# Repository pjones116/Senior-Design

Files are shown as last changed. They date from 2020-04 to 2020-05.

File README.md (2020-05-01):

# User Manual
## __Back End and Physical Setup__:
#### Image the Raspberry Pi:
•	The official guide for this process can be found here: https://www.raspberrypi.org/documentation/installation/installing-images/

•	For the purposes of this generation of the product, our team used Raspbian GNU / Linux 9, also known as Stretch, but the OS version for the system should have little influence on proper operation

#### Connect the Pi to basic peripherals and boot:
•	Connect mouse and keyboard via USB

•	Connect HDMI cable to external monitor

•	Connect Ethernet cable for wired network connection (optional, only needed for setup)

•	Connect the Pi to wall power adapter

•	Boot into Raspbian or preferred OS

#### Enable system interfaces:
•	Once booted in, click on the Raspberry Pi symbol to open the system menu

•	Navigate down to “Preferences” and open the “Raspberry Pi Configuration” tab

•	Navigate to the “Interfaces” tab and ensure that Camera, SSH, VNC, and I2C are enabled

#### Setup remote monitoring webserver on the Pi:
•	Pagekite is used to assign hostnames to outward facing VNC addresses to make remote monitoring possible from anywhere

•	Sign up for Pagekite here: https://pagekite.net/signup/

•	Follow the guide at the following page: https://pagekite.net/support/quickstart/

•	Once initial setup is completed, two kites should be added by executing the following from command line:

  -	“python2 pagekite.py --add 80 <site_name>.pagekite.me”
  
  -	“python2 pagekite.py --add 5900 raw:vnc.<site_name>.pagekite.me:5900”

•	Both of these hostnames need to be up at all times and, after their creation, can be launched using the following from command line:

  -	“python2 pagekite.py 80 <site_name>.pagekite.me”

  -	“python2 pagekite.py port# raw:vnc.<site_name>.pagekite.me:5900”

•	This application’s website contains instructions on how to run this program from startup, if desired

#### Setup VNC monitoring on remote machine:
•	Download VNC Viewer by RealVNC on the machine the Pi will be monitored from

•	Navigate to preferences and locate the “Proxy” tab

•	Select the options to “Use these proxy settings”

•	Enter the following values:

  -	Server: vnc.<site_name>.pagekite.me:443

  -	Type: HTTP Connect

  -	User / Pass: pi / raspberry (initial image user / pass)

•	You can then connect via VNC to the Pi via the address vnc.<site_name>.pagekite.me:5900

#### Share SSH keys between the Pi and data server:
•	From the Raspberry Pi, generate an SSH key by executing the following on command line: 
  
  -	“ssh-keygen”

•	Then copy this key to the remote data server by executing the following: 

  -	“ssh-copy-id –i ~/.ssh/id_rsa.pub <X.X.X.X>”

•	This step is absolutely vital for this application’s performance and can be tested by attempting to SSH to the remote data server without password:

  -	“ssh <X.X.X.X>”

#### Setup Redis-Server on the Pi:
•	Redis-Server is used implement a job queuing process processing data from the application

•	The setup process can be found at the following: https://habilisbest.com/install-redis-on-your-raspberrypi

•	Once Redis is properly setup, this queue webserver should be run constantly when data is being processed by doing the following from command line:

  -	“redis-server”

#### Setup SQL Server on data server:
•	Both SQL Server and the SQL Command Line Tools should be installed on the data server

•	The following process should be followed:

  -	https://docs.microsoft.com/en-us/sql/linux/quickstart-install-connect-ubuntu?view=sql-server-ver15
  
  -	Please note, an Ubuntu based server is currently deployed for this group, but Microsoft provides installation guides for these tools for most common operating systems

•	Once SQL Server is properly setup, a table with the following columns and data types should be created (Please note: currently, all variables are VARCHAR type)

  -	Timestamp – VARCHAR
  
  -	pH – FLOAT
  
  -	Conductivity – FLOAT
  
  -	Temperature – FLOAT
  
  -	Humidity – FLOAT
  
  -	Image Name – VARCHAR

#### Setup ImageMagick on data server (optional):
•	ImageMagick can be used to view images via X server when a machine establishes an SSH connection with the data server

•	The following shows the setup process for a typical Ubuntu machine: https://linuxconfig.org/how-to-install-imagemagick-7-on-ubuntu-18-04-linux

•	In order to launch the X server on startup of the SSH session, simply type the following when first connecting:

  -	“ssh <user>@<X.X.X.X> -X”

•	Then, in order to display any image type the following on command line, once inside the image’s directory:

  -	“display <filename>.<extension>”

•	If continual issues occur with displaying images, make sure the $DISPLAY environment variable is set correctly on your data server by executing the following:

  -	“export DISPLAY=localhost:0.0”

#### Setup full peripherals:
•	Connect the PiCamera via GPIO ribbon the Pi’s camera port

•	Connect the Atlas T3 Tentacle hat to the Pi’s GPIO header and attach the appropriate Atlas sensors to their respective serial cable header

•	Attach the GPIO ribbon cable to the T3’s GPIO header extension, then connect a breadboard on the ribbon cable

•	Connect all additional sensors to their respective GPIO ports on the ribbon cable’s breadboard connector

•	Attach battery powering system, lower device into enclosure and properly attach sensors and camera to arms

#### Download application package from Github:
•	Download full application (3 scripts) from Github and create an appropriate environment for them (i.e. create and name a folder solely for holding the scripts)

•	Establish a folder called “capstone” on the Pi’s desktop, which will be used for storing the processed data and images

#### Download Python packages for scripts:
•	Execute the following from the command line to install a Python package:

  -	“pip install <pkg_name>”

•	The following is a list and description of all Python packages needed to run this application:

  -	time – Used to implement wait periods, timings
  
  -	sys – Used to force clean exit from script on error outs
  
  -	OS – Used to execute CMD commands from inside script
  
  -	subprocess – Used to call CMD subprocesses from inside script (i.e. rsync calls)
  
  -	picamera – Used to operate and manipulate Pi camera
  
  -	datetime – Used to establish time stamped naming conventions
  
  -	RPi.GPIO – Used to operate Pi GPIO ports
  
  -	Adafruit_DHT – Used to gather temperature and humidity data from Adafruit DHT11 or DHT22 sensor
  
  -	IO – Used to create and implement filestreams
  
  -	fcntl – Used to interact with I2C parameters for Atlas sensors
  
  -	string – Used to interact with and manipulate strings
  
  -	copy – Used to move I2C parameters between addresses by copying values under certain specified conditions
  
  -	RQ – Used to simply implement a Redis job queue (note: this is unofficial)
  
  -	Redis – Used to connect to Redis queue from inside script (note: this is official)
  
  -	Pyodc – Used to setup script connection to SQL Server 

#### Edit variable information in scripts:
• atlas.py – queue name for Redis queue, username and IP for data server, rsync folder name on data server

•	atlas_upload.py – queue name for Redis queue, connection details for SQL Server on data server, schema and table names for SQL Server table

#### Script details:
•	atlas.py:

  -	Takes sensor readings and images, submits data to Redis queue and uploads CSV and images to directory on data server
  
  -	Run at user’s discretion (i.e. run when user wants to run an experiment)
  
  -	Execute with the following: “python atlas.py”

•	atlas_worker.py:

  -	Acts as middleman and takes enqueued data to be submitted to queue and pushed to the correct script
  
  -	This script can be left running at all times due to low CPU and memory impact, as it will process results any time they are submitted
  
  -	Execute with the following: “python atlas_worker.py <queue_name>”

•	atlas_upload.py:

  -	Uploads the queued data to the remote data server’s SQL Server table
  
  -	NEVER interacted with by the user, this script is only used when called from the main atlas.py

## __System Operational Notes__:
•	Python version to be used – 2.7.13

  -	Though Python 2.7 is going to be considered fully deprecated soon, the only way that the current build works with Atlas’ provided I2C software is if it is used
  
  -	NOTE: ensure that the relevant version of Pip is deployed for installing packages for the correct version of Python

•	Constantly running scripts

  -	The easiest way to implement the technologies discussed in this guide without too much maintenance is to have several scripts     continually run (or to add them to your Bash configuration for launch on startup)
  
  -	It is recommended that both Pagekite addresses (main and VNC), atlas_upload, and redis-server stay continually running

•	This enables the application to run with end-to-end success by only executing the main atlas.py

## __Front End Setup__:
•	This project is uses a React front end app that is written in JavaScript.

•	Currently the code can be seen on a front-end GUI. However, due to some impediments related to the Coronavirus it is very basic and there is no user experience.

•	Information and documentation for React can be found here: https://reactjs.org/

•	The connection to the front-end is made in the Index.js file

•	To setup the environment for into the terminal and run the following:

  -	mkdir “folder name”
  
  -	touch package.json
  
  -	npm init -y

• Insert the code into the index.js file

• Install the following packages:
  
  -	yarn add express 
  
  - yard add mysql 
  
  -	yarn add cors
  
  -	yarn add react

•	In order to run the front end code, run the following command: ‘nodemon Index.js’

• Ensure that you are in the correct folder when running the code

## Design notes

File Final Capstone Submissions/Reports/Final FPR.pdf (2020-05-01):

The George Washington University School of Engineering and Applied Science Department of Electrical and Computer Engineering

ECE 4920W - 30

Final Product Review
Low Cost, Remote Data Acquisition Platform for In Situ Biological and Fluidic Measurements

Rachel Zaltz, Computer Engineering Connor Kraft, Computer Engineering Phillip Jones, Electrical Engineering

Professor Aslani, Professor Bulusu April 22, 2020

Final Design Review

Abstract (R)

A low-cost data acquisition platform will be designed and assembled to increase the ease of dynamic in situ data collection from confined isolated environments such as incubators. The aim of this project is to record humidity, temperature, PH, turbidity, time-stamped imaging, and various other sensor data at user-specified intervals. The device will remain physically independent of the space outside the incubator by using a modular power supply and network connection. The device will run independently of a power supply for the duration of the experiment and wirelessly send the desired data to a remote user. The device will advance research in cellular and polymetric interactions with indirect measurement and imaging in incubators.

Table of Contents
Table of Contents | 3
1. | Introduction (R) | 6
2. | Impacts and Effects (P) | 6
2.1. | Public Health | 6
2.2. | Safety | 6
2.3. | Welfare | 6
2.4. | Global | 6
2.5. | Social | 7
2.6. | Cultural | 7
2.7. | Environmental | 7
2.8. | Economic | 7
3. | Overall System Requirements and Specifications (All) | 7
4. | Approach to Overall Design (C) | 8
4.1. | Current Design | 8
4.2. | Evolution of Current Design | 8
5. System and Subsystems (Modules) Functional Diagrams, Requirement and Specifications
| (All) | 9
5.1. | Raspberry Pi Subsystem Requirements and Specifications | 9
5.2. | Sensor Subsystem Requirements and Specifications | 9
5.2.1. Raspberry Pi GPIO Controller Description | 10
5.2.2. LED Lights Description | 10
5.2.3. Raspberry Pi Camera Description | 11
5.2.4. Pi Tentacle Hat Description | 11
5.2.5. Conductivity Sensor Description | 11
5.2.6. pH Sensor Description | 11
5.2.7. Temperature & Humidity Sensor Description | 11
5.3. | User Interface Subsystem Requirements and Specifications | 11
5.4. | Power Management Subsystem Requirements and Specifications | 12
5.4.1. Charge Protection Circuit Requirements and Specifications | 12
5.4.2. Battery Requirements and Specifications | 12
5.4.3. Voltage Converter Circuit Requirements and Specifications | 12
6. | Module Design (All) | 13
6.1. | Raspberry Pi Subsystem | 13
6.2. | Sensor Interface Subsystem | 13

6.3. | User Interface Subsystem | 13
6.4. | Power Management Subsystem | 14
7. | Design Changes Since FDRF | 14
8. | Module and System Tests | 14
8.1. | Raspberry Pi Subsystem Tests | 15
8.2. | Sensor Subsystem Tests | 15
8.3. | User Interface Subsystem Tests | 15
8.4. | Power Management Subsystem Tests | 16
9. | Applicable Standards (All) | 16
9.1. | Probes | 16
9.2. | Raspberry Pi | 17
9.3. | System | 17
9.4. | Hardware | 17
9.5. | Protocols | 17
10. | Summary and Conclusions (R) | 18
11. | References | 18
12. | Appendices | 18
12.1. Timeline Estimation and Milestones | 18
12.2. Economic Analysis | 20
12.3. Part List | 22
12.4. Qualifications of Key Personnel | 23
12.5. Intellectual Contributions | 24
12.6. Teaming Arrangements | 24
12.7. User Manual | 24
12.8. Mechanical Drawings | 28
12.9. GUI Screenshots | 31
12.10. Code | 31

Table of Figures:

1. Introduction (R)
The low-cost data-acquisition platform will be designed to increase dynamic in situ data collection in confined and isolated environments. Currently, when an experiment is performed within an incubator for a long period of time, lab technicians are unable to open the confined environment until the experiment has been completed in its entirety. This results in a loss of crucial data points as the experiment is progressing within the incubator. Currently, the data cannot be obtained during the duration of the experiment and this results in the loss of many crucial data points. A low-cost data acquisition platform would increase data collection in in situ environments.
Currently, there are only a few products that solve the issue at hand. Some of the best products are from Dickson Data, such as the DicksonOne. These products only allow for a small set of sensors and lack more advanced sensor technology and cameras. They are also very expensive, with the cheapest model being $350. Each individual sensor costs over 100 dollars and requires a paid subscription to use some of the more advanced features. Overall, a product does not exist that meets all of the design requirements for this task.
This project looks to implement a system which can gather data within a closed incubator and send that data to a user on any remote computer. The data is gathered from multiple sensors including temperature, humidity, pH, turbidity, and time stamped images. This data is gathered at a time interval which can be specified by the user to allow for greater flexibility of the system. When data is not being gathered, sensors are turned off in order to save power and conserve energy. This data is then sent to a computer using a Wifi connection so that it may be viewed by the user.
2. Impacts and Effects (P)
2.1. Public Health
Our product has no overall effects or impacts on public health in general. While research generated by the project or by employment of our device may positively impact public health, our system itself does not improve public health.
2.2. Safety
See reasoning for public health.
2.3. Welfare
Our project is also heavily focused on the promotion of ease of access of data acquisition. Having a fully wireless module that performs all functionality via remote GUI, with no impact on environment conditions inside the experiment, is an extremely productive option to the alternatives. This will increase the opportunities to have full experiment length data measurement, as well as make the data acquisition process smoother in general.
2.4. Global
As spoken about in the welfare section, this project will make overall data acquisition easier for the user. In addition, users will be able to run data acquisition experiments in areas without wired power; however, the data would have to be transferred locally at some point instead of being dumped wirelessly. This could have potential to drive this system as an alternative for taking large-scale equipment to remote research sites.

2.5. Social
This project will make taking data from environments like an incubator more convenient and hands free, increasing the social wellbeing of the communities it will be deployed in.
2.6. Cultural
Our project has little to no impact on the cultural standing of the community.
2.7. Environmental
Our project has little to no impact on the environment, as opposed to alternative options. As stated before, our project itself has no impact on this, but the research where it is employed could very well be beneficial.
2.8. Economic
Our project has an economic benefit, in that the cost effectiveness of the product is much more productive than its next best alternatives. Due to the low cost to employ this device, money will be able to be reallocated to other research needs.
3. Overall System Requirements and Specifications (All)
System Level Requirements | System Level Specifications
The device will operate with a lithium ion battery pack. | The device shall be able to run on a lithium ion battery pack.
The device will have a long battery life, so the device does not have to be removed from the incubator. | The device shall be able to last on the battery pack for the duration of the experiment (minimum 1 day - maximum 4 weeks).
The device will take pictures of the test environment. | A Pi camera must be used to take pictures of the test environment at user specified intervals.
The device will have a light source for the test environment. | The device must conserve battery by only using the lights when needed (e.g., taking a picture) or when the user specifies.
The device will conserve battery with 2 different modes: sleep and active. | The device shall be in sleep mode when measurements and images are not being taken.
The device will measure pH. | The device shall be able to measure the pH of the solution from 0 to 14 at +/-

| 0.001 increments using a pH probe, with an accuracy of +/- 0.002.
The device will measure humidity and temperature. | The device shall be able to measure humidity from 20 to 80% with an accuracy of +/- 5% and temperature from 0 to 50 degrees C with an accuracy of +/- 2 degrees C using Pi HAT sensors.
Th device will measure turbidity. | A turbidity probe shall be used to measure the amount of light scattered by the solids in the solution.
Th device will measure electrical conductivity. | A conductivity probe shall be used to measure the electrical conductivity of the solution from 5 to 200,000 micro-S/cm, with an accuracy of +/- 2%.
The device will be accessible to a remote user. | The device shall send data to a GUI that can be accessed remotely through a desktop and mobile application.
Communication will be enabled via Wifi on the device. | The device should be able to send data to a computer via the built in Wifi module on the Raspberry Pi 3+.
4. Approach to Overall Design (C & R)
4.1. Current Design
The goal of the project is to design a system which can gather data in a closed environment and send this data wirelessly to a remote user. The data gathered is specified by the sensors in section 6.2. The system can do this with only one input from the user, the data collection rate (every 30 seconds), and how long to gather data for (12 hours). These inputs and outputs are outlined in Figure 2 below. The flow of data from the user to system and system to user can be seen in Figure 1 below. Further, Figures 3-5 details the modules in more depth.
4.2. Evolution of Current Design
This design has shifted gears slightly amidst the current pandemic. Due to some constraints, not all testing was completed, and the user interface functions on a very minimal level. The overall goal of the project is maintained; however, we were not able to implement our design in a real testing space due to social distancing measures.

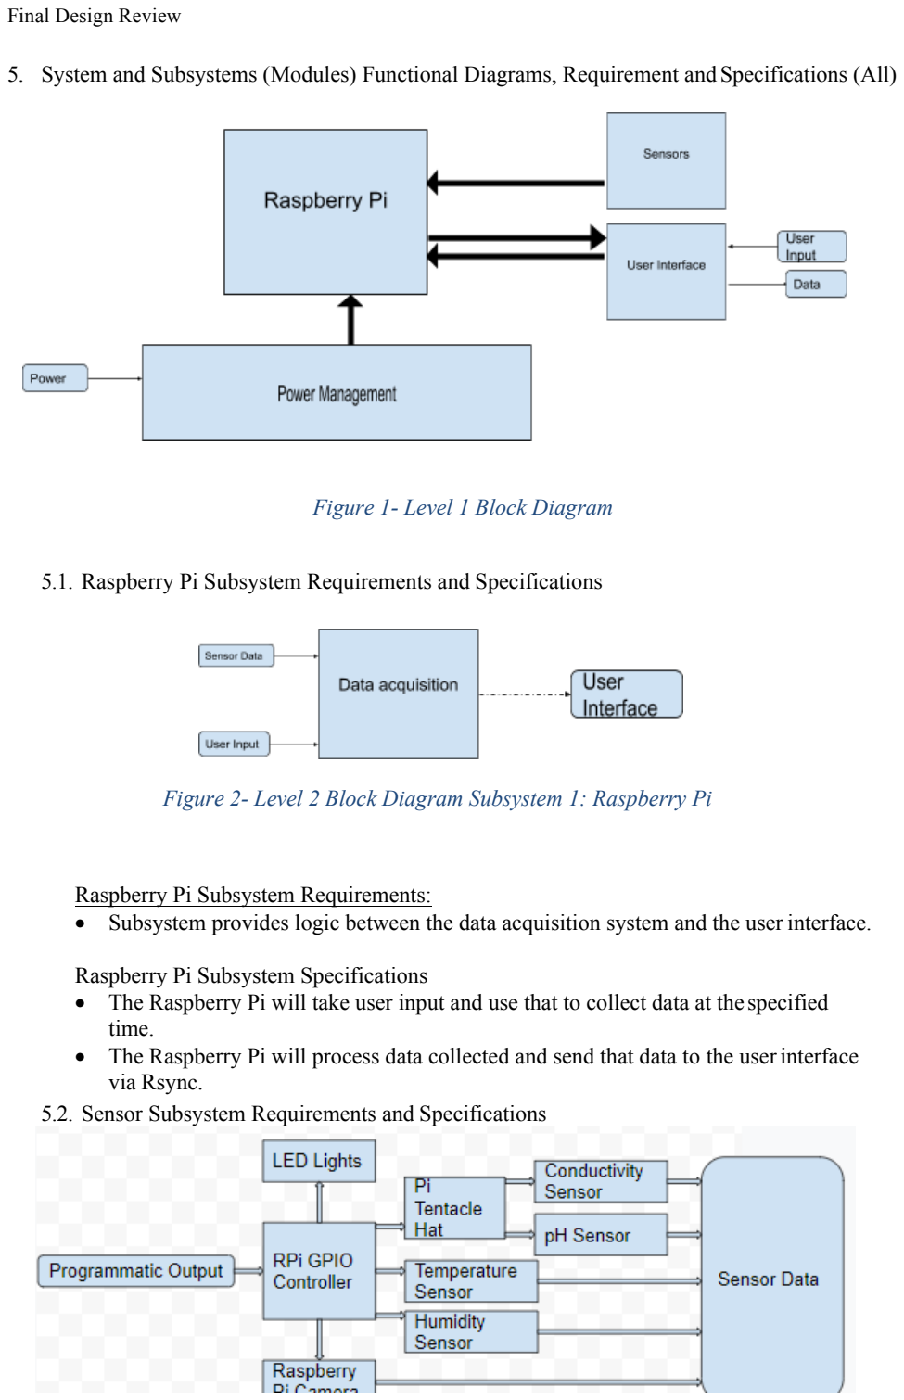
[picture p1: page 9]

5. System and Subsystems (Modules) Functional Diagrams, Requirement and Specifications (All)

Figure 1- Level 1 Block Diagram

5.1. Raspberry Pi Subsystem Requirements and Specifications

Figure 2- Level 2 Block Diagram Subsystem 1: Raspberry Pi

Raspberry Pi Subsystem Requirements:
- Subsystem provides logic between the data acquisition system and the user interface.

Raspberry Pi Subsystem Specifications
- The Raspberry Pi will take user input and use that to collect data at the specified time.
- The Raspberry Pi will process data collected and send that data to the userinterface via Rsync.
5.2. Sensor Subsystem Requirements and Specifications

Figure 3 - Level 2 Block Diagram Subsystem 2: Sensors

Sensor Subsystem Requirements:
- Subsystem provides data acquisition for system, using the inputs given via user program instructions.
- Subsystem sends user data back to program data stream.

Sensor Subsystem Specifications:
- The Raspberry Pi GPIO controller will translate the programmatic read instructionsto sensors readable inputs.
- The LED will inform each time the system is specified to take a reading.
- The Raspberry Pi camera will take a photo at each read interval.
- The Raspberry Pi Tentacle T3 hat will relay programmatic read instructions to the conductivity and pH sensors.
- The EZO conductivity and pH sensors will gather and relay sample conductivity and pH data at specified intervals.
- The temperature and humidity sensor will process and relay environmental condition data.
5.2.1. Raspberry Pi GPIO Controller Description
The Raspberry Pi GPIO controller provides the basis for sending and reading voltage levels to and from sensors. When provided with corresponding voltage, sensors will return their read value to the header. This information is then reformatted for user or program access.
5.2.2. LED Lights Description
A red LED shall be used to provide a notification system for the user. The light will blink each time a read is made on the system’s sensor array.

5.2.3. Raspberry Pi Camera Description
The camera connects to the MIPI camera serial interface on the Raspberry Pi via a 15- pin ribbon cable. It can take 3280 × 2464-pixel images.
5.2.4. Pi Tentacle Hat Description
The hat connects to the GPIO of the Raspberry Pi and outputs 3 BNC connections. It includes chips to handle the configuration of each individual sensor. It passes through the GPIO pins to allow for stacking of hats or connection of other parts.
5.2.5. Conductivity Sensor Description
The Atlas Scientific Conductivity Probe measures system level of conductivity from 5 to 200,000 uS/cm, with an accuracy of +/- 2%. The sensor will relay the environmental or sample level of conductivity at the user specified interval.
5.2.6. pH Sensor Description
The Atlas Scientific pH probe measures system levels of pH from 0 to 14, with an accuracy of +/- 0.002. The sensor will relay the environmental or sample level of pH at the user specified interval.
5.2.7. Temperature & Humidity Sensor Description
The Adafruit DHT11 probe measures environmental temperature and humidity. The humidity sensor measures from 20 to 90 room humidity with an accuracy of +/- 5%. The temperature sensor measures from 0 to 50 degrees Celsius with an accuracy of +/- 2%. The sensor will relay the environmental temperature and humidity data at user specified intervals.
5.3. User Interface Subsystem Requirements and Specifications

Figure 4 - Level 2 Block Diagram Subsystem 3: User Interface

User Interface subsystem requirements
- The data must be easily accessible to a remote user.

User Interface subsystem specifications
- The user must be able to access all experiment data from the system.

5.4. Power Management Subsystem Requirements and Specifications

Figure 5 - Level 2 Block Diagram Subsystem 4: Power Management

Power management subsystem requirements
- System supplies voltage to Raspberry Pi.
- System charges the battery.

Power management subsystem specifications
- The Raspberry Pi takes 5 Volts.
- A wall outlet will charge the battery.
5.4.1. Charge Protection Circuit Requirements and Specifications Charge protection circuit requirements
- Circuit optimizes the safe charging of the battery.

Charge protection circuit specifications
- The charge protection circuit will stop charging the battery at 100% charge.
- The charge protection circuit will monitor the charge level in each cell and keep each cell at the same level of charge.
5.4.2. Battery Requirements and Specifications
Battery Requirements
- The battery will supply power to the Raspberry Pi.

Battery Specifications
- The battery will charge from the charge protection circuit.
- The battery will output 12 Volts, which it will supply to the voltage conversion circuit.
- The battery will hold at least 200ah of charge
5.4.3. Voltage Converter Circuit Requirements and Specifications
Voltage converter circuit Requirements
- Circuit converts battery output to a lower voltage to supply Raspberry Pi.

Voltage converter Specifications
- The voltage converter will take 7V from the output of the battery and output 5V to power the Raspberry Pi.
6. Module Design (All)
6.1. Raspberry Pi Subsystem
The Raspberry Pi is the central computation and storage module for the system. It receives power from the power management module and receives input from programmatic user instructions. It runs experimental scripts and gathers data via input from attached sensors. It stores and exports data via Rsync / GUI / local storage.
A Raspberry Pi was chosen for this subsystem over other alternatives such as Beagleboard and Arduino. The Raspberry Pi was chosen for its low cost and its ability to meet the other specifications required by the project.
6.2. Sensor Interface Subsystem
The sensor module works via the Raspberry Pi’s GPIO header outputting programmatic instructions. Temperature and humidity are measured via sensor straight from this header, while all Atlas sensor data is taken through conversion to I2C over BNC via the Tentacle T3 Hat. In addition, the Pi Camera is powered from another GPIO slot on board. All received data from the sensors and camera are then stored locally and manipulated by programmatic instruction.
6.2.1. Camera
The Raspberry Pi camera was chosen due to the ease of connecting it to the Raspberry Pi. Other cameras were investigated, such as ones connected by USB, but none met the project needs.
6.2.2. Tentacle Hat
This module was chosen based on the choice of sensors. This module exists because of the following two sensors, so no alternatives were considered.
6.2.3. Conductivity Sensor
This sensor was chosen in conjunction with the client. Alternatives were not considered.
6.2.4. pH Sensor
This sensor was chosen in conjunction with the client. Alternatives were not considered.
6.2.5. Temperature and Humidity Sensor
Initially, a simple thermistor and different off-the-shelf humidity sensors were investigated. We decided on the Adafruit DHT1 due to its ease of use combining both sensors into one and the ease of connecting it to the system.
6.3. User Interface Subsystem
Input for the UI system consists only of data and information about each experiment being related remotely from central Raspberry Pi. The UI receives this information and presents it to the user visually and enables the user to interact with and download that data.

The UI will receive this information in real time via webserver file transfer.

6.4. Power Management Subsystem
This module supplies power to the rest of the system. This module was designed with the need for the system to be able to operate in spaces with no wall power. The charge protection circuit receives power from the wall and distributes it evenly across all cells in the battery, stopping when the cells are full. The charge protection circuit regulates the output of the battery, preventing them from being fully discharged. The voltage converter changes the voltage outputted by the battery to the 5V required by the Raspberry Pi.
6.4.1. Charge Protection Circuit
No alternatives have been considered for this module. The system requires a battery to run and needs a way to safely charge.
6.4.2. Battery
No alternatives have been considered for this module. A battery is a requirement for our system to run. A power test was not conducted due to the restrictions of the pandemic.
6.4.3. Voltage Converter Circuit
No alternatives have been considered for this module. The Raspberry Pi requires 5V to run and a voltage converter is needed to regulate the voltage from the battery.
7. Design Changes Since FDRF
Since the completion of the FDR, design changes have primarily been related to the data pipeline structure for this project. These changes were born out of a necessity to facilitate user interaction with this system, as well as to provide redundant options for data transfer and storage. In order to complete both of these tasks, a Redis queue was added for chronning data transfer jobs and keeping them active in the event of some kind of failure, and a remote data server was added for storage and organization.

At the current time, gathered data is collected and stored in labeled local directories on the Raspberry Pi. All relevant timestamps, sensor data, and image names are then queued by Redis and transferred to a SQL Server database running on the server. For the sake of redundancy, all relevant Raspberry Pi local files are then synced to a directory on this server. Redis allows for consistency in transfer and maintains the operating status of said transfer jobs, and the remote data server allows for easy data presentation by the front end and acts as a secondary storage location.

It is important to note that other than these changes, the primary structure and design for this project has remained consistent. Though completion of work related to the front end and battery circuit was hindered extremely by the current state of the Coronavirus outbreak, these portions of the project are still integral to its functionality and purpose. In order to craft a successful end-to-end product, these sections need to be implemented.

8. Module and System Tests

Note: while the tests discussed below were supposed to be run, due to the current Coronavirus outbreak affecting certain aspects of this project’s completion, alternate testing strategies were devised. An overall system test was performed with varying parameters for overall time and sensor reading interval. Our team felt that this was a productive testing plan to complete what could be done with the current situation.

The three tests devised to test the overall system, sensor accuracy over time, data transfer behavior, and system behavior under load are as follows:

- 1 hour test – 360 sensor readings
- 2.5 hour test – 50 sensor readings
- 8 hour test – 97 sensor readings
8.1. Raspberry Pi Subsystem Tests
Tests:
- Pi Stress Test - Run a worst-case scenario experiment and check that the Raspberry Pi continuously sends the data to the user and storage solution.
- Pi / Remote Storage Stress Test - Run alternate test case scenario with large set of data; and ensure the Raspberry Pi is able to complete a run of transferring multiple megabyte files continuously.

Specifications:
- The Raspberry Pi will take user input and use that to collect data at the specified time.
- The Raspberry Pi will process the data collected and send that data to the user interface via rsync.
8.2. Sensor Subsystem Tests
Tests:
- Stress Test - Run a worst-case scenario experiment (4 weeks sampling every 2 seconds) and check that the sensors collect data over the whole time period.
- Use sensors to measure known variables (such as a known room temperature or standard pH solution) to check accuracy.

Specifications:
- The Raspberry Pi GPIO controller will translate the programmatic read instructionsto the sensors.
- The LED will inform the user of each time the system takes a reading.
- The Raspberry Pi camera will take a photo at each read interval.
- The Raspberry Pi Tentacle T3 hat will relay the programmatic instructions to the Atlas sensors.
- The sensors will relay environmental condition data at each specified time interval.
8.3. User Interface Subsystem Tests
Tests:
- Test functionality of visually interactive components by activating themand observing outputs.
- Verify the application’s responsiveness on screen sizes for tablets (width: 1024/768 pixels), monitors (width: infinite pixels), and mobile devices (width: 480/320 pixels).

Specifications:
- The user must be able to access and observe current system status.
- The user must be able to access and observe all sensor readings and pictures taken over the course of an entire experiment.

Note: Due to the Coronavirus outbreak not all the User Interface tests were completed. In an ideal world where there is more time these tests should still be done.

8.4. Power Management Subsystem Tests
Tests:
- Verify that the maximum output of the subsystem is 5 volts to the Raspberry Pi and any attached equipment.
- Run a worst-case scenario experiment (4 weeks sampling every 2 seconds) and check that power is applied at appropriate levels for the entirety of the experiment.
- Monitor the shape of the battery during charging and system operation and observe any alterations that occur.
Specifications:
- The system will supply 5 volts to the Raspberry Pi and any attached equipment.
- The battery must last for the maximum possible duration of an experiment; for this project, that length is anticipated to be a maximum of 4 weeks.
- The charge protection circuit will stop charging the battery when it has reached 100% charge.
9. Applicable Standards (All)
9.1. Probes
NSF/ANSI-51 Section 4.1
Pi / Remote Storage Stress Test - Run alternate test case scenario with large set of data; and ensure the Raspberry Pi can complete a run of transferring multiple megabyte files continuously.

NSF/ANSI-51 Section 7.6.1
Glass and glass-like materials. Such materials shall not be used for direct food contact that are also subject to impact by hard objects during use such as countertops, tabletops, cutting boards, cooking surfaces, and food preparation utensils. This standard has the same use case as the previous one.

73/23/EEC
The aim of this directive is to ensure that electrical equipment cannot be placed on the market if, when installed and maintained, it endangers the safety of persons, domestic animals or property. This standard is for the probes and it ensures that there is no danger due to being electrocuted.

ISO/IEC 17025
ISO/IEC 17025 enables laboratories to demonstrate that they operate competently and generate valid results, thereby promoting confidence in their work both nationally and around the world. It also helps facilitate cooperation between laboratories and other bodies by generating wider acceptance of results between countries. This standard is applicable to this project since our product will be used in labs to gather results.
9.2. Raspberry Pi
EC 60950-1:2005
Mains and battery-powered general low voltage electrical equipment must follow safety standards related to temperature exposure, dust and moisture exposure, etc. This standard applies to operation of RaspberryPi 3B+.

EN 55022 CISPR 22
There are radio disturbance characteristic limits and methods of measurement for electrical equipment. This establishes uniform requirements for radio disturbance, standard operating conditions, and standard interpretations of testing results. It applies to all standard and networked operations of RaspberryPi 3B+.

EN 55024 CISPR 24
Tests and places standardized limitations for device electrostatic discharge, surges, power frequency magnetic fields, power interruptions, and RF interference.

Covers standard and networked operations of RaspberryPi 3B+ and all attached electrical equipment.

EN 300 328 V2.1.1
Wideband transmission systems; data transmission equipment operating in the 2.4 GHz ISM band using wide band modulation techniques. Limitations on output RF power and behavioral maintenance of networked equipment. Applies to networked operation of RaspberryPi 3B+.
9.3. System
IEC 62311:2019
Covers appropriate maintenance of equipment-generated exposure to electric, magnetic, and electromagnetic for devices operating from 0 Hz to 300 GHz. Standard limitations are applied to equipment via localized standards, applicable to this standard. Applies to the operation of full system.

EN 55032 CISPR 32
Procedural standard for limiting levels of spurious signals generated by multimedia equipment for electromagnetic protection in industrial, commercial, and residential environments. Applies to the operation of full system.
9.4. Hardware
ISO 4032:2012
Hexagon regular nuts (style 1) — Product grades A and B. Used in sizing holes for nuts and bolts to assemble enclosure.
9.5. Protocols
UM10204
Philips Semiconductors (now NXP Semiconductors) developed a simple bidirectional 2-wire bus for efficient inter-IC control. This bus is called the Inter-IC or I2C-bus. This standard is used for communicating between the Raspberry Pi and the sensors.

RFC 4256
The Secure Shell Protocol (SSH) is a protocol for secure remote login and other secure network services over an insecure network. This document describes a general-purpose authentication method for the SSH protocol, suitable for interactive authentications where the authentication data should be entered via a keyboard. This standard is useful to our project since it is how we are going about sending data wirelessly using Rsync.
10. Summary and Conclusions (R)

This semester, all major tasks with the sensors were completed; sensors were integrated fully with the back-end code. In addition to this, a front-end GUI and enclosure modeling were drafted in preparation for full system operation. On the front-end the user can fully see all the data as opposed to having to look in the database now. Final drawings for the enclosure were done, however not everything was printed due to the current situation. The system is ready to be tested for an experiment if time would allow.

This semester, several improvements were made to the overall efficiency and functionality of the system’s data pipeline. A Redis queue was added to monitor and schedule the submission of data to the project’s newly added data server. This server was deployed into a redundant storage scheme where all information stored locally on the Raspberry Pi is then subsequently transferred to it via Rsync. In addition to this, a SQL Server was deployed on this remote storage space to be implemented by the graphical interface. This SQL database serves not only as an efficient way to serve the information to a user over the internet, but also as a quick lookup table to ensure that the system is functioning properly via system diagnostics read at every sensor interval. Overall, the last semester has yielded great productivity in the track to completion of this project. The data pipeline is fully prepared to be deployed both online and as a storage solution for a wider-spread audience.

11. References

Unlock the Power of Pay. (n.d.). Retrieved from https://www.salary.com/

12. Appendices
12.1. Timeline Estimation and Milestones

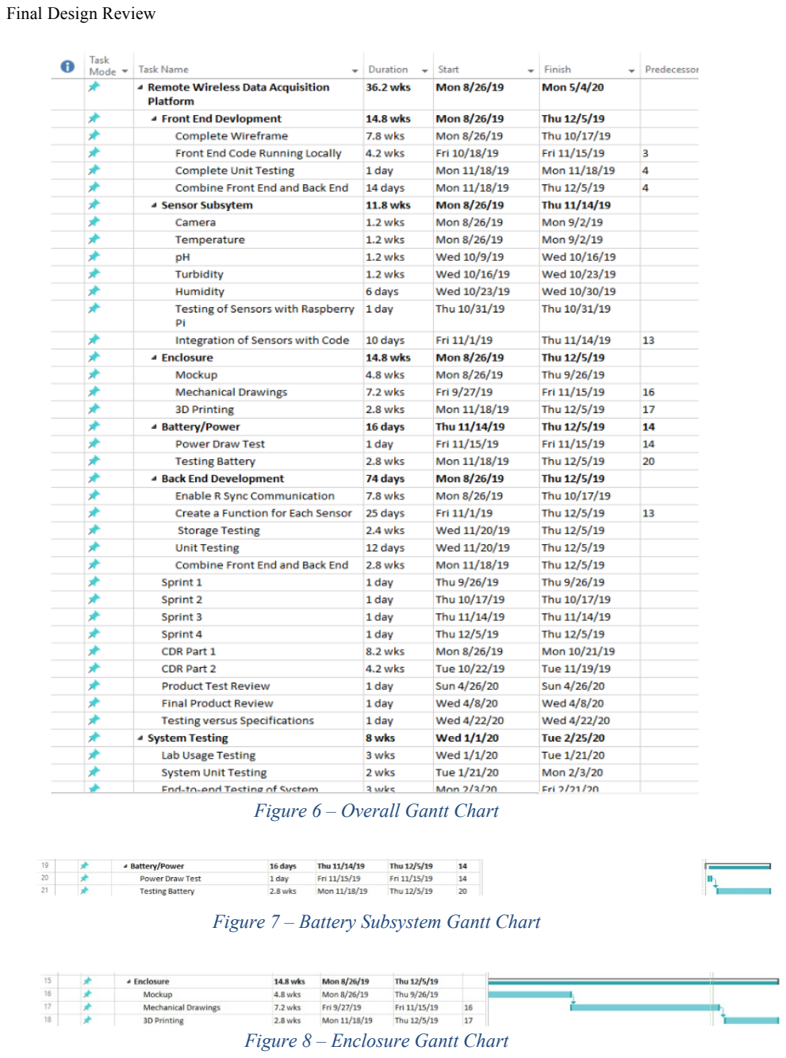
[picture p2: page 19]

Figure 6 – Overall Gantt Chart

Figure 7 – Battery Subsystem Gantt Chart

Figure 8 – Enclosure Gantt Chart

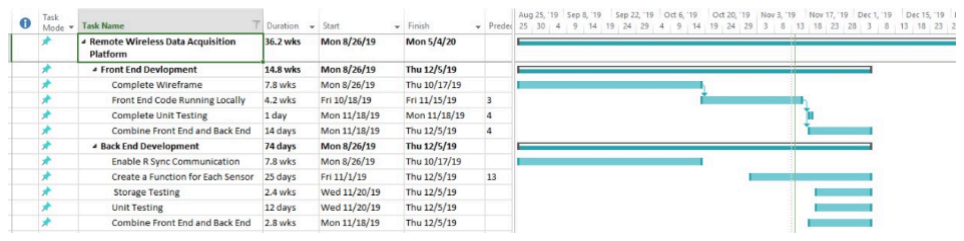
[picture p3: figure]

Figure 9 – Front/Back End Gantt Chart

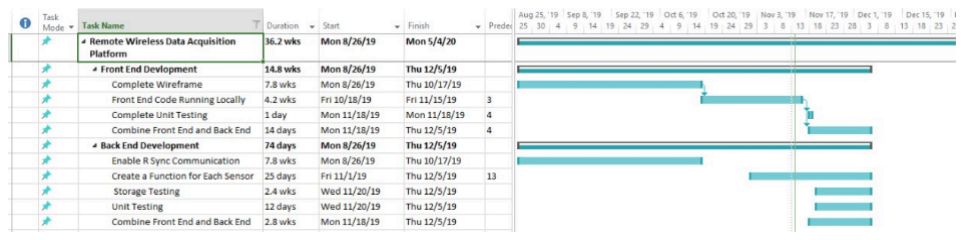
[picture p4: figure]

Figure 10 – Sensor Subsystem Gantt Chart

12.2. Economic Analysis

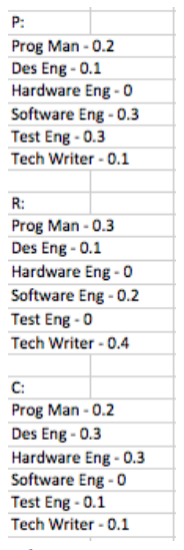
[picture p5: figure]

Figure 11 – Working Hours per Person

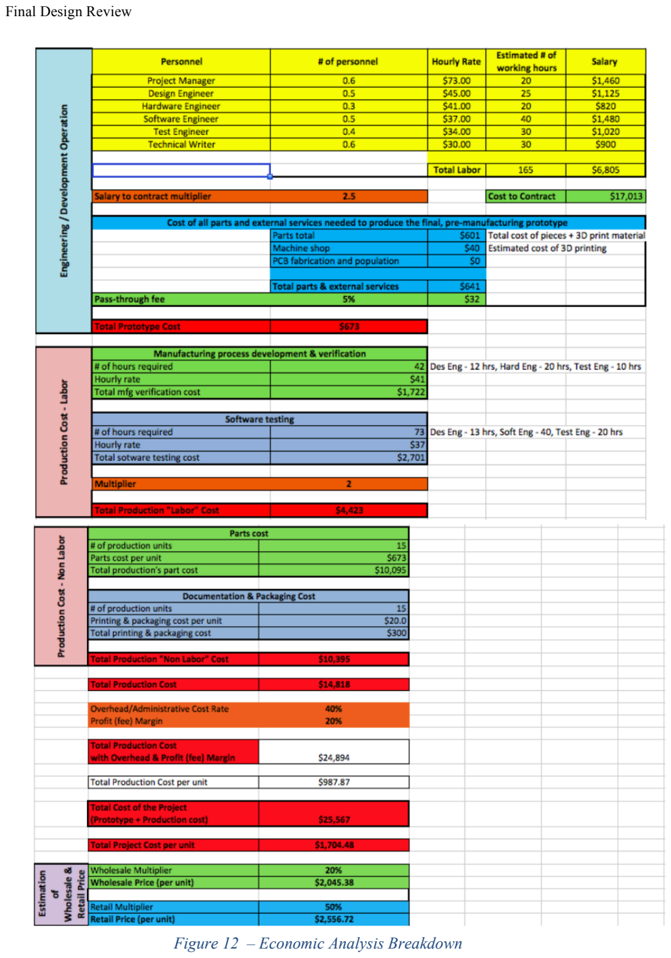
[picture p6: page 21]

Figure 12 – Economic Analysis Breakdown

This product would be offered as a good, with all the desired sensors and attachments wrapped in with the cost of the Raspberry Pi and the software application. The retail price of this product would be $2,556.72, as can be seen in the figure above. An additional option to use this software as a standalone option could also be released, where the user would provide their own Raspberry Pi and sensors, configuring the device on their own.

12.3. Part List
Part Name | Description | Manufacturer | Manufactur er’s Part # | Supplier | Cost ($) | Quantity
Single Board Computer | Raspberry Pi 3B + | Raspberry Pi | 3775 | Adafruit | 35.00 | 1
GPIO Extender | RPi GPIO Breakout Expansion Board & Ribbon | Arceli | ZB2L3 | Amazon | 7.99 | 1
Breadboard | Solderless Breadboard Kit | REXQualis | RQ-BK-002 | Amazon | 9.86 | 1
Resistor | 220 Ohm | E-Projects | 32121600 | Amazon | 6.00 | 1 (100 resistors)
Temperature-Humidity Sensor | DHT11 | Adafruit | 100502 | Amazon | 9.61 | 1
LED | Red Diffused LED | Jameco | 2152155 | Jameco | 0.59 | 5

Conductivity Sensor | Conductivity K 1.0 Kit | Atlas Scientific | EC-KIT-1.0 | Atlas Scientific | 215.00 | 1
pH Sensor | pH Kit | Atlas Scientific | KIT-101P | Atlas Scientific | 164.00 | 1
GPIO Hat | Tentacle T3 | Whitebox Labs for Atlas Scientific | TEN-T3 | Atlas Scientific | 105.00 | 1
Camera | RPi Camera Module V2-8 MP | Raspberry Pi | RPI-CAM-V2 | Amazon | 24.80 | 1
Ethernet Cable | CAT 6 Ethernet Cable | Mediabridge | 31-299-10B | Amazon | 5.84 | 1
12.4. Qualifications of Key Personnel
Rachel Zaltz’s qualifications make her a stellar candidate to work on this project. Her course work at the GWU includes Operating Systems, Microprocessors, Embedded Systems, Intro to C Programming will aid her in this project. [DZ2] Rachel’s wide knowledge of different programming languages allow her to adapt quickly. Her internship experience includes an extensive amount of front-end development, which will be useful towards the end of the project in building a user- friendly interface to view all the data.
Connor Kraft’s qualifications allow him to be a good team member. His work teaching children STEM classes over the summer, including teaching Python and Raspberry Pi courses, will aid in the overall design and troubleshooting of the project. Further, the teaching of 3D design and printing will be useful towards the end of the project when building an enclosure. His coursework at GWU includes Microprocessors, Embedded systems, and Circuit theory will all help in the hardware aspect of this project.
Phillip Jones has numerous experiences that are directly related to this project that will greatly facilitate with him making contributions. His coursework at GWU includes several Electronics Design classes, Microprocessor Systems, Introduction to C Programming, and Circuit Design. Phillip has worked for two semesters with SEAS computing as a Raspberry Pi student workshop director and has additional supplementary work experience with the same company. Lastly, he has extensive programming experience working on an automated data pipeline web application for Gamma Ray Burst behavioral analysis.

12.5. Intellectual Contributions
1. The group will purchase all sensors, power supply, and any other necessary fabrication materials.
a. The group will use these to fabricate all the above modules.
b. Sensors will be tested and calibrated for accuracy
2. We will design, implement, and test code to gather the sensor data.
3. We will implement Rsync to access the previously mentioned data wirelessly.
a. We will test this system with a wide variety of file sizes and file amounts
4. We will design, implement, and test a GUI that interacts with the previously mentioned code.
12.6. Teaming Arrangements
Throughout this project, all team members will work as a cohesive unit to ensure the product is designed properly. Each team member will lead one part of the project:
- Phillip will lead the group in implementing the physical code on the hardware.
- Connor will oversee testing the code and evaluating the results. He will also design an enclosure to house the final project.
- Rachel will build the GUI to display the data. She will also facilitate all documentation throughout the duration of the project.
12.7. User Manual

Setup Steps:
Image the Raspberry Pi:
- The official guide for this process can be found here: https://www.raspberrypi.org/documentation/installation/installing-images/
- For the purposes of this generation of the product, our team used Raspbian GNU / Linux 9, also known as Stretch, but the OS version for the system should have little influence on proper operation

Connect the Pi to basic peripherals and boot:
- Connect mouse and keyboard via USB
- Connect HDMI cable to external monitor
- Connect Ethernet cable for wired network connection (optional, only needed for setup)
- Connect the Pi to wall power adapter
- Boot into Raspbian or preferred OS

Enable system interfaces:
- Once booted in, click on the Raspberry Pi symbol to open the system menu
- Navigate down to “Preferences” and open the “Raspberry Pi Configuration” tab
- Navigate to the “Interfaces” tab and ensure that Camera, SSH, VNC, and I2C are enabled

Setup remote monitoring webserver on the Pi:
- Pagekite is used to assign hostnames to outward facing VNC addresses to make remote monitoring possible from anywhere
- Sign up for Pagekite here: https://pagekite.net/signup/
- Follow the guide at the following page: https://pagekite.net/support/quickstart/

- Once initial setup is completed, two kites should be added by executing the following from command line:
- “python2 pagekite.py --add 80 <site_name>.pagekite.me”
- “python2 pagekite.py --add 5900 raw:vnc.<site_name>.pagekite.me:5900”
- Both of these hostnames need to be up at all times and, after their creation, can be launched using the following from command line:
- “python2 pagekite.py 80 <site_name>.pagekite.me”
- “python2 pagekite.py port# raw:vnc.<site_name>.pagekite.me:5900”
- This application’s website contains instructions on how to run this program from startup, if desired

Setup VNC monitoring on remote machine:
- Download VNC Viewer by RealVNC on the machine the Pi will be monitored from
- Navigate to preferences and locate the “Proxy” tab
- Select the options to “Use these proxy settings”
- Enter the following values:
- Server: vnc.<site_name>.pagekite.me:443
- Type: HTTP Connect
- User / Pass: pi / raspberry (initial image user / pass)
- You can then connect via VNC to the Pi via the address vnc.<site_name>.pagekite.me:5900

Share SSH keys between the Pi and data server:
- From the Raspberry Pi, generate an SSH key by executing the following on command line:
- “ssh-keygen”
- Then copy this key to the remote data server by executing the following:
- “ssh-copy-id –i ~/.ssh/id_rsa.pub <X.X.X.X>”
- This step is absolutely vital for this application’s performance and can be tested by attempting to SSH to the remote data server without password:
- “ssh <X.X.X.X>”

Setup Redis-Server on the Pi:
- Redis-Server is used implement a job queuing process processing data from the application
- The setup process can be found at the following: https://habilisbest.com/install-redis-on-your-raspberrypi
- Once Redis is properly setup, this queue webserver should be run constantly when data is being processed by doing the following from command line:
- “redis-server”

Setup SQL Server on data server:
- Both SQL Server and the SQL Command Line Tools should be installed on the data server
- The following process should be followed:
- https://docs.microsoft.com/en-us/sql/linux/quickstart-install-connect-ubuntu?view=sql-server-ver15
- Please note, an Ubuntu based server is currently deployed for this group, but Microsoft provides installation guides for these tools for most common operating systems
- Once SQL Server is properly setup, a table with the following columns and data types should be created
- Timestamp – VARCHAR

- pH – FLOAT
- Conductivity – FLOAT
- Temperature – FLOAT
- Humidity – FLOAT
- Image Name – VARCHAR

Setup ImageMagick on data server (optional):
- ImageMagick can be used to view images via X server when a machine establishes an SSH connection with the data server
- The following shows the setup process for a typical Ubuntu machine: https://linuxconfig.org/how-to-install-imagemagick-7-on-ubuntu-18-04-linux
- In order to launch the X server on startup of the SSH session, simply type the following when first connecting:
- “ssh <user>@<X.X.X.X> -X”
- Then, in order to display any image type the following on command line, once inside the image’s directory:
- “display <filename>.<extension>”
- If continual issues occur with displaying images, make sure the $DISPLAY environment variable is set correctly on your data server by executing the following:
- “export DISPLAY=localhost:0.0”

Setup full peripherals:
- Connect the PiCamera via GPIO ribbon the Pi’s camera port
- Connect the Atlas T3 Tentacle hat to the Pi’s GPIO header and attach the appropriate Atlas sensors to their respective serial cable header
- Attach the GPIO ribbon cable to the T3’s GPIO header extension, then connect a breadboard on the ribbon cable
- Connect all additional sensors to their respective GPIO ports on the ribbon cable’s breadboard connector
- Attach battery powering system, lower device into enclosure and properly attach sensors and camera to arms

Download application package from Github:
- Download full application (3 scripts) from Github and create an appropriate environment for them (i.e. create and name a folder solely for holding the scripts)
- Establish a folder called “capstone” on the Pi’s desktop, which will be used for storing the processed data and images

Download Python packages for scripts:
- Execute the following from the command line to install a Python package:
- “pip install <pkg_name>”
- The following is a list and description of all Python packages needed to run this application:
- time – Used to implement wait periods, timings
- sys – Used to force clean exit from script on error outs
- OS – Used to execute CMD commands from inside script
- subprocess – Used to call CMD subprocesses from inside script (i.e. rsync calls)
- picamera – Used to operate and manipulate Pi camera
- datetime – Used to establish time stamped naming conventions
- RPi.GPIO – Used to operate Pi GPIO ports

- Adafruit_DHT – Used to gather temperature and humidity data from Adafruit DHT11 or DHT22 sensor
- IO – Used to create and implement filestreams
- fcntl – Used to interact with I2C parameters for Atlas sensors
- string – Used to interact with and manipulate strings
- copy – Used to move I2C parameters between addresses by copying values under certain specified conditions
- RQ – Used to simply implement a Redis job queue (note: this is unofficial)
- Redis – Used to connect to Redis queue from inside script (note: this is official)
- Pyodc – Used to setup script connection to SQL Server

Edit variable information in scripts:
- atlas.py – queue name for Redis queue, username and IP for data server, rsync folder name on data server
- atlas_upload.py – queue name for Redis queue, connection details for SQL Server on data server, schema and table names for SQL Server table

Script details:
- atlas.py:
- Takes sensor readings and images, submits data to Redis queue and uploads CSV and images to directory on data server
- Run at user’s discretion (i.e. run when user wants to run an experiment)
- Execute with the following: “python atlas.py”
- atlas_worker.py:
- Acts as middleman and takes enqueued data to be submitted to queue and pushed to the correct script
- This script can be left running at all times due to low CPU and memory impact, as it will process results any time they are submitted
- Execute with the following: “python atlas_worker.py <queue_name>”
- atlas_upload.py:
- Uploads the queued data to the remote data server’s SQL Server table
- NEVER interacted with by the user, this script is only used when called from the main atlas.py

System Operational Notes:
- Python version to be used – 2.7.13
- Though Python 2.7 is going to be considered fully deprecated soon, the only way that the current build works with Atlas’ provided I2C software is if it is used
- NOTE: ensure that the relevant version of Pip is deployed for installing packages for the correct version of Python
- Constantly running scripts
- The easiest way to implement the technologies discussed in this guide without too much maintenance is to have several scripts continually run (or to add them to your Bash configuration for launch on startup)
- It is recommended that both Pagekite addresses (main and VNC), atlas_upload, and redis-server stay continually running
! This enables the application to run with end-to-end success by only executing the main atlas.py

Front End Code Notes:
- This project is uses a React front end app that is written in JavaScript.
- Currently the code can be seen on a front-end GUI. However, due to some impediments related to the Coronavirus it is very basic and there is no user experience.
- Information and documentation for React can be found here: https://reactjs.org/
- The connection to the front-end is made in the Index.js file
- To setup the environment for into the terminal and run the following:
- mkdir “folder name”
- touch package.json
- npm init -y
- Insert the code into the index.js file
- Install the following packages:
! yarn add express
! yard add mysql
! yarn add cors
! yarn add react
- In order to run the front end code, run the following command: ‘nodemon Index.js’
- Ensure that you are in the correct folder when running the code.
12.8. Mechanical Drawings

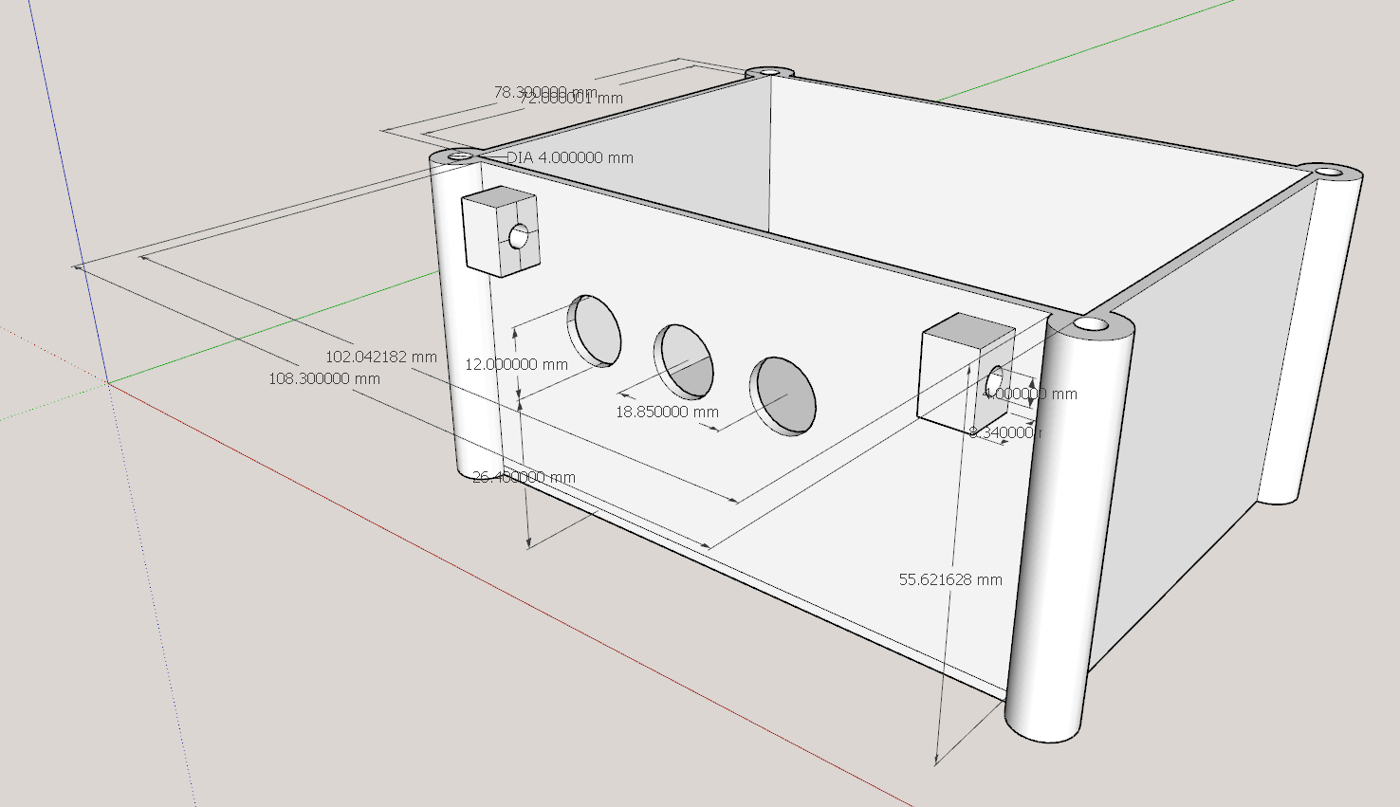
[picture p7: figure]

Figure 13 – Enclosure Bottom Piece

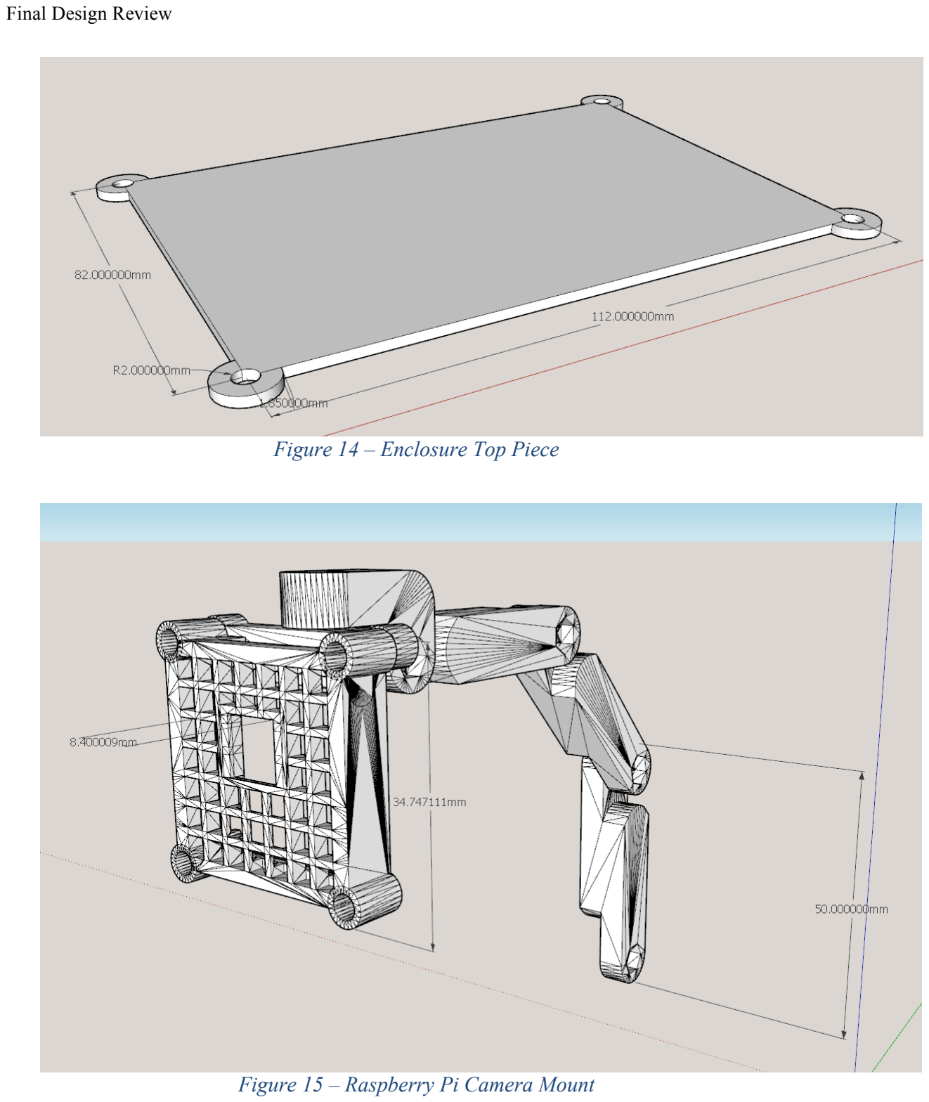
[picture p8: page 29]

Figure 14 – Enclosure Top Piece

Figure 15 – Raspberry Pi Camera Mount

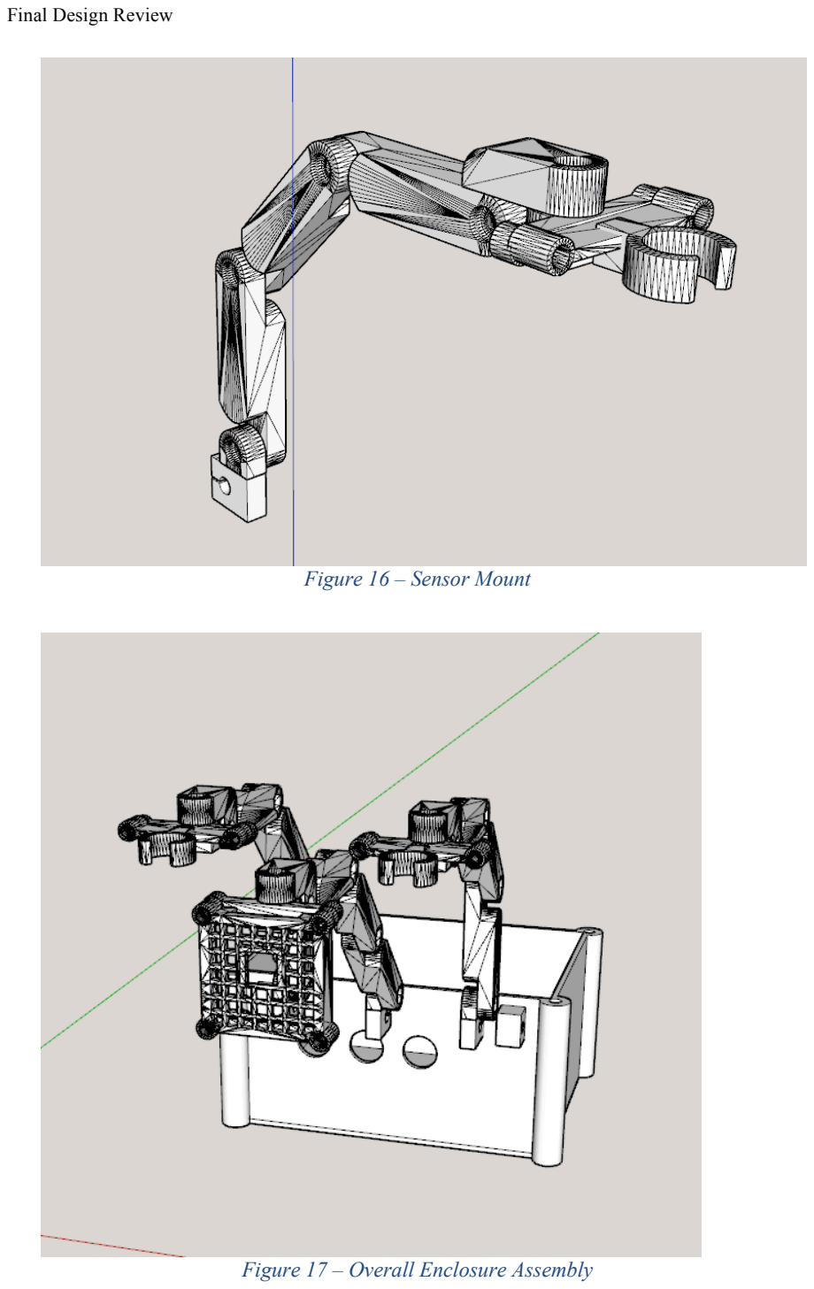
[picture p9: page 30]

Figure 16 – Sensor Mount

Figure 17 – Overall Enclosure Assembly

12.9. GUI Screenshots

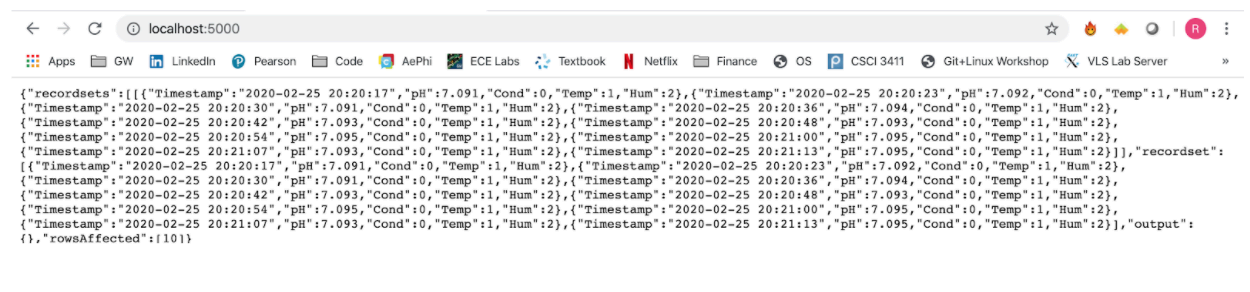
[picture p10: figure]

Figure 18 – Frontend Output

12.10. Code

// written by Rachel Zaltz
function ignoreFavicon(req, res, next) { if (req.originalUrl === '/favicon.ico') { res.status(204).json({nope: true});
} else {
next();
}
}
var express = require('express'); var cors = require('cors');
var app = express();
var React = require('react'); app.use(ignoreFavicon);
app.use(cors());
app.get('/', function (req, res) { var sql = require("mssql");

// config for your database var config = {
server:X.X.X.X',
user: 'XXXX',
port:XXXX,
password: 'XXXX',
database: 'XXXX'
};
// connect to your database sql.connect(config, function (err) {

if (err) console.log(err);
// create Request object
var request = new sql.Request();
// query to the database and get the records
request.query('select * from capstone.testing.example', function (err, recordset) { if (err) console.log(err)
// send records as a response
res.send(recordset);

});
});
});

// Listen on a specific host via the HOST environment variable var host = process.env.HOST || 'localhost';
// Listen on a specific port via the PORT environment variable var port = process.env.PORT || 5000;
var cors_proxy = require('cors-anywhere'); cors_proxy.createServer({
originWhitelist: [], // Allow all origins requireHeader: ['origin', 'x-requested-with'],
removeHeaders: ['cookie', 'cookie2']
}).listen(port, host, function() {
console.log('Running CORS Anywhere on ' + host + ':' + port); });
var server = app.listen(5000, function () {
console.log('Server is running..');
});
Connection from GUI to Back End Code

'''
ECE4925W - Final Capstone Submission, Spring 2020
Phillip Jones, Connor Kraft, Rachel Zaltz

final_atlas - takes data, organizes storage structure, submits queue request for transportation to storage server
final_atlas_worker - takes resulting data and actually submits to queue
final_atlas_upload - submits data to sql database on storage server

For detailed questions on packages used / scripts, please see User Manual Appendix and the FPR, in general

'''

import pyodbc | # Use to make Python connection to SQL Server on storage server
from rq import Queue | # Use to implement Redis queue actions
from rq import get_current_job | # Use to get information on submitted jobs
from redis import Redis | # Use to make Python connection to Redis server on RPi
from time import sleep | # Use to make program stop for period

def upload_to_db(data):
redis_conn=Redis()
q=Queue('atlas',connection=redis_conn,default_timeout=300)
# The following information currently works with the provided server

# Contact Mark Aglipay if you arrive with issues on the server / with the SQL Server application conn = pyodbc.connect(driver='{FreeTDS}',

server=X.X.X.X',
port='XXXXX',
database='XXXX',
uid='XXXX',
pwd='XXXX')
cursor=conn.cursor()

# Following data is taken from the constructed dictionary in final_atlas.py

# Data is out of order, but submits to server in correct order, due to how the queueing orders the information

# Sleep is used to reduce load on server between sensor readings / data commits tval=str(data.values()[3])

phval=str(data.values()[4])
condval=str(data.values()[5])
tempval=str(data.values()[0]) humval=str(data.values()[2])
imgval=str(tval + '.png')
expname=str(data.values()[1])
cursor.execute('INSERT INTO XXXX.XXXX.XXXX (Timestamp,pH,Cond,Temp,Hum,img_name,exp_name) VALUES (?,?,?,?,?,?,?)', tval,phval,condval,tempval,humval,imgval,expname)
conn.commit()
sleep(5)
return

Final Atlas Upload Python Code

'''
ECE4925W - Final Capstone Submission, Spring 2020
Phillip Jones, Connor Kraft, Rachel Zaltz

final_atlas - takes data, organizes storage structure, submits queue request for transportation to storage server
final_atlas_worker - takes resulting data and actually submits to queue
final_atlas_upload - submits data to sql database on storage server

For detailed questions on packages used / scripts, please see User Manual Appendix and the FPR, in general

All information in Class AtlasI2C was taken from Atlas Scientific's sample program for I2C device communication
'''
from atlas_upload import upload_to_db | # Called script from our application package
import time | # Use for actual timing
from time import sleep | # Use to stop scripts for period of time
import sys | # Use to control system level exit of program
import os | # Enables user to act on files outside program
import subprocess | # Use to invoke call to cmd
import picamera | # Use to control RPi camera
import datetime | # Use to get current datetime info
import RPi.GPIO as GPIO | # Use to interact with RPi GPIO pins
import Adafruit_DHT | # Stock module for temp/humidity sensor
import io | # Use to create file streams
from io import open | # Use to open files in file streams
import fcntl | # Use to access I2C parameters
import string | # Use to parse strings

import copy | # Use to implement copy as function of Python
from rq import Queue | # Allows for Redis job queueing
from rq import get_current_job | # Use for getting information about current job
from redis import Redis | # Use to make connection to Redis server
import psutil | # Use to produce system level diagnostic info about RPi

# Open camera, set resolution

camera = picamera.PiCamera()
camera.resolution = '1080p'

# Open GPIO pin 21, set for output as "flash" for photo GPIO.setmode(GPIO.BCM)

GPIO.setwarnings(False)
GPIO.setup(21,GPIO.OUT)

# Initialize temp/hum sensor

sensor = Adafruit_DHT.DHT11
pin = 23

# Initialize queue, open connection to atlas queue

redis_conn = Redis()
q = Queue('atlas', connection=redis_conn, default_timeout=300)

'''
All information in AtlasI2C is taken from the provided configuration of Atlas' I2C devices

This information can be altered as desired, please tread lightly when doing this,
as this can result in significant differences in operation for these sensors

In addition, this version has been altered, as the provided build encountered problems with sensor configuration and operation
'''

class AtlasI2C:
long_timeout = 1.5 | # Timeout needed to query readings / calibrations
short_timeout = 0.3 | # Timeout for regular commands
default_bus = 1 | # Default RPi I2C bus
default_address = 98 | # Default sensor address
LONG_TIMEOUT_COMMANDS = ("R", "CAL") # Wait for long period while reading SLEEP_COMMANDS = ("SLEEP", ) # Assign sleep commands

def __init__(self, address = default_address, bus = default_bus):
# Init 2 file streams, for reading and writing

self._address = address or self.default_address
self.bus = bus or self.default_bus
self._long_timeout = self.long_timeout
self._short_timeout = self.short_timeout
self.file_read = io.open(file="/dev/i2c-{}".format(self.bus), mode="rb", buffering=0) self.file_write = io.open(file="/dev/i2c-{}".format(self.bus), mode="wb", buffering=0) self.name = ""

def set_i2c_address(self, addr):
# Set I2C communications to slave address I2C_SLAVE = 0x703

fcntl.ioctl(self.file_read, I2C_SLAVE, addr) fcntl.ioctl(self.file_write, I2C_SLAVE, addr) self.address = addr

def write(self, cmd):
# Appends null character and send string over I2C cmd += "\00"

self.file_write.write(cmd.encode('latin-1'))

def handle_raspi_glitch(self, response):
if self.app_using_python_two():
return list(map(lambda x: chr(ord(x) & ~0x80), list(response))) else:
return list(map(lambda x: chr(x & ~0x80), list(response[1:])))

def app_using_python_two(self):
return sys.version_info[0] < 3

def get_response(self, raw_data):
if self.app_using_python_two():
response = [i for i in raw_data if i != '\x00' ] else:
response = raw_data

return response

def response_valid(self, response): valid = True
error_code = None
if(len(response)>0):
if self.app_using_python_two(): error_code = str(ord(response[0])) else:
error_code = str(response[0])

if error_code != '1':
valid = False

return valid, error_code

def get_device_info(self): if(self.name == ""):
return str(self.address)
else:
return str(self.address) + " " + self.name

def read(self, num_of_bytes=31):
raw_data = self.file_read.read(num_of_bytes)

response = self.get_response(raw_data=raw_data)
is_valid, error_code = self.response_valid(response=response)

if is_valid:
char_list = self.handle_raspi_glitch(response[1:])
result = "Success " + self.get_device_info() + ": " + str(''.join(char_list)) else:
result = "Error " + self.get_device_info() + ": " + error_code

return result

def get_command_timeout(self, command):
timeout = None
if command.upper().startswith(self.LONG_TIMEOUT_COMMANDS): timeout = self._long_timeout
elif not command.upper().startswith(self.SLEEP_COMMANDS): timeout = self.short_timeout

return timeout

def query(self, command):
self.write(command)
current_timeout = self.get_command_timeout(command=command) if not current_timeout:
return "sleep mode"
else:
time.sleep(current_timeout) return self.read()

def close(self):
self.file_read.close()
self.file_write.close()

def list_i2c_devices(self):
prev_addr = copy.deepcopy(self._address) i2c_devices = []
for i in range(0,128):
try:
self.set_i2c_address(i)
self.read(i)
i2c_devices.append(i)
except IOError:
pass
self.set_i2c_address(prev_addr)

return i2c_devices

def main():
# Allow for user input of experiment name

# MUST BE IN QUOTES, NO SPACES experiment_name = input("Input the name of the experiment: ")

# Timestamp name of data log file and enable write

d2 = datetime.datetime.now()
# Create local data dump folder

os.system('mkdir /home/pi/Desktop/capstone/' + experiment_name + '.' + d2.strftime('%Y.%m.%d-%H.%M.%S'))
# Create local data dump csv

csv = open('/home/pi/Desktop/capstone/'+ experiment_name + '.'+ d2.strftime('%Y.%m.%d-%H.%M.%S') + '/' + d2.strftime('%Y.%m.%d-%H.%M.%S') +'.csv', 'a')
# Create I2C port object

device = AtlasI2C()
try:
# FOR LOOP HARD CODED, CHANGE IN FUTURE (NUMBER OF READS)

# This loop turns on/off flash, takes photo in between, reads from each sensor

# Sensor info and system diagnostics are then organized and submitted to the Redis queue for storage server

# All info is then also saved to a local CSV, to be also transferred to storage server via rsync for i in range(0,5):

d = datetime.datetime.now()
print('\n')
print(d)
pict = d.strftime('%Y.%m.%d-%H.%M.%S')
picn = ('/home/pi/Desktop/capstone/' + experiment_name + '.'+ d2.strftime('%Y.%m.%d-%H.%M.%S') + '/' + pict + '.png')
print('Light on\t')
GPIO.output(21,GPIO.HIGH)
sleep(0.5)
print('Taking picture\t')
camera.capture(picn)
print('Light off, taking sensor data')
GPIO.output(21,GPIO.LOW)
#humidity, temperature = Adafruit_DHT.read_retry(sensor,pin)

# CHANGE THESE TEMP/HUM HARD CODED VALUES IN FUTURE temperature = 1.00

humidity = 2.00
device.set_i2c_address(99)
phstring = device.query('R')[11:] phstring = str(phstring)
device.set_i2c_address(100) condstring = device.query('R')[12:]
condstring = str(condstring)

data = {
'time' : d.strftime('%Y-%m-%d %H:%M:%S'), 'pH': phstring,
'conductivity': condstring,
'temperature': temperature,
'humidity': humidity,
'exp_name': experiment_name
}
log_data = {
'CPU usage' : psutil.cpu_percent(),

'CPU temp' : subprocess.check_output(['vcgencmd', 'measure_temp'], stderr=subprocess.STDOUT),
'RAM usage' : psutil.virtual_memory()[2]
}
job = q.enqueue(upload_to_db, data, result_ttl=86400) print('Current job on queue: %s\n' % (job.id,))
# Parsing and handling this information is both annoying and difficult,

# I reccomend leaving this scheme for the entirety of the project

# i.e. I reccomend not moving away from CSV as a secondary storage method csv.write(unicode('experiment: ' + str(data['exp_name']) + ',')) csv.write(unicode('time: ' + str(data['time']) + ','))

csv.write(unicode('pH: ' + str(data['pH']) + ',')) csv.write(unicode('conductivity: ' + str(data['conductivity']) + ',')) csv.write(unicode('temperaure: ' + str(data['temperature']) + ',')) csv.write(unicode('humidity: ' + str(data['humidity']) + ',\n')) csv.write(unicode('CPU usage: ' + str(log_data['CPU usage']) + ',')) csv.write(unicode('CPU ' + str(log_data['CPU temp'])[:-1] + ',')) csv.write(unicode('RAM usage: ' + str(log_data['RAM usage']) + ',')) csv.write(unicode('\n\n'))
sleep(3)
continue

# Proper exit: close camera, file, and invoke cmd to employ SSH file sync # Then exit at a system level

camera.stop_preview()
csv.close()
subprocess.call(['rsync','-avrPzh','/home/pi/Desktop/capstone','-e','ssh -p 22','user@X.X.X.X:~/'])
sys.exit()

# Improper exit: close camera, file, and brute force exit system

except KeyboardInterrupt:
camera.stop_preview()
csv.close()
print('\nClosed by keyboard interrupt.') sys.exit()

if __name__ == '__main__':
main()

Final Atlas Python Code

'''
ECE4925W - Final Capstone Submission, Spring 2020
Phillip Jones, Connor Kraft, Rachel Zaltz

final_atlas - takes data, organizes storage structure, submits queue request for transportation to storage server
final_atlas_worker - takes resulting data and actually submits to queue
final_atlas_upload - submits data to sql database on storage server

For detailed questions on packages used / scripts, please see User Manual Appendix and the FPR, in general

This program was provided entirely via the RQ setup guide

Launch Redis server first, type the following on cmd: "redis-server"

Launch with the following on cmd: "python final_atlas_worker.py atlas"

This names the queue that jobs will be submitted to

This script acts as middleman transport, can be left running at all times (script works automatically) '''

import sys
from rq import Connection, Worker

with Connection():
qs = sys.argv[1:] or ['default']
w = Worker(qs)
w.work()

Final Atlas Worker Python Code

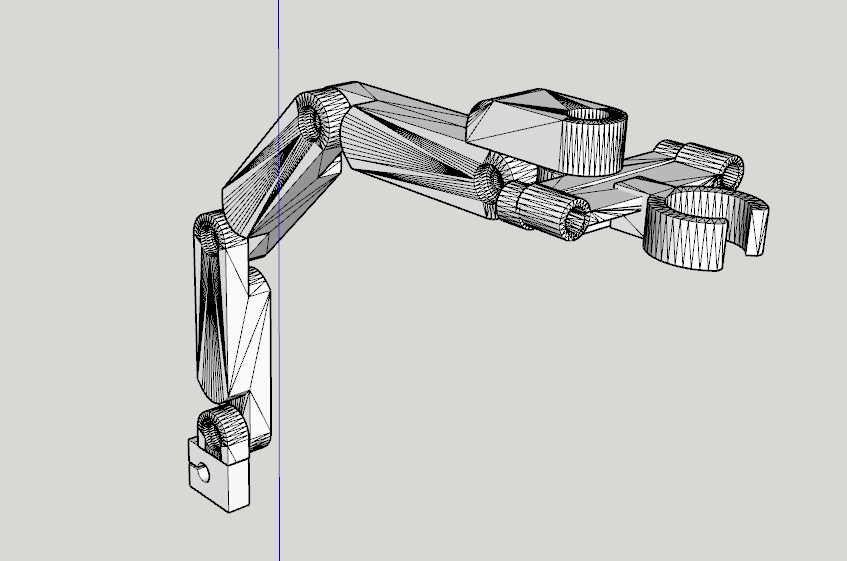
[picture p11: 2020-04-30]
Mechanical_Designs/Sensor_arm.PNG

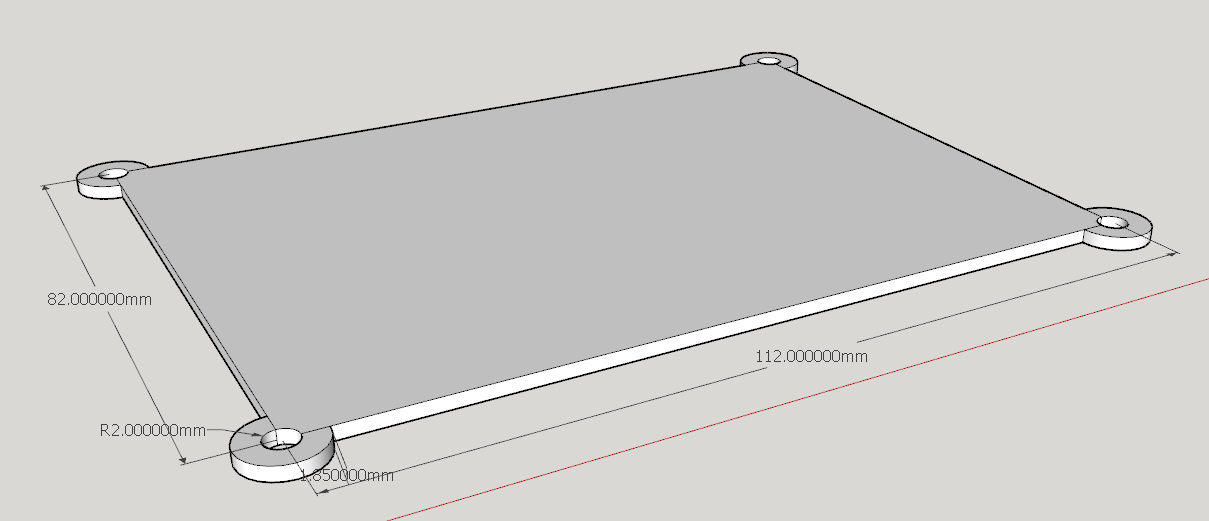
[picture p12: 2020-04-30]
Mechanical_Designs/case_top.PNG

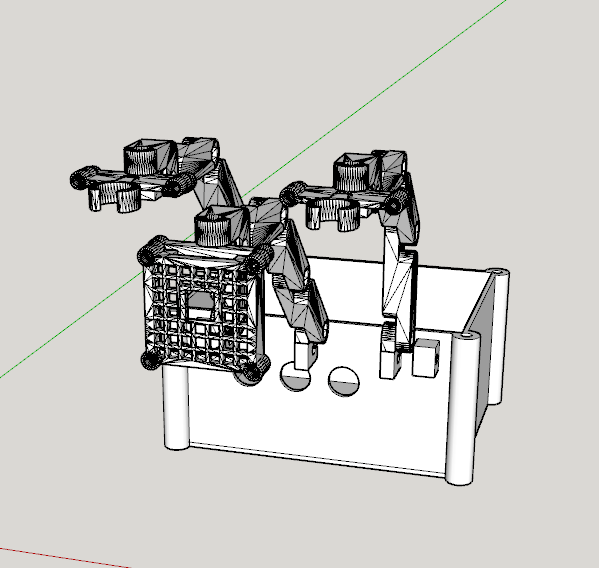
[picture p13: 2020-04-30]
Mechanical_Designs/All_together.PNG

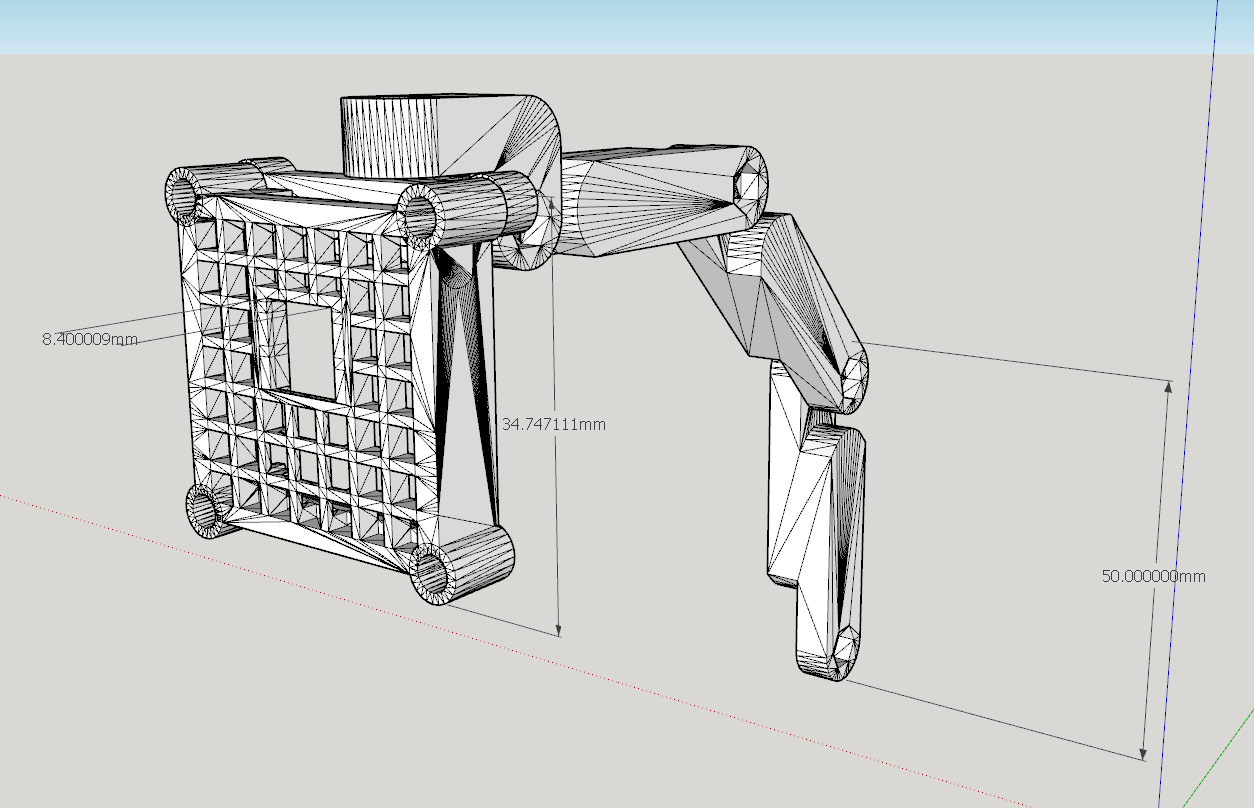
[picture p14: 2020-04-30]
Mechanical_Designs/Pi_camera_arm.png

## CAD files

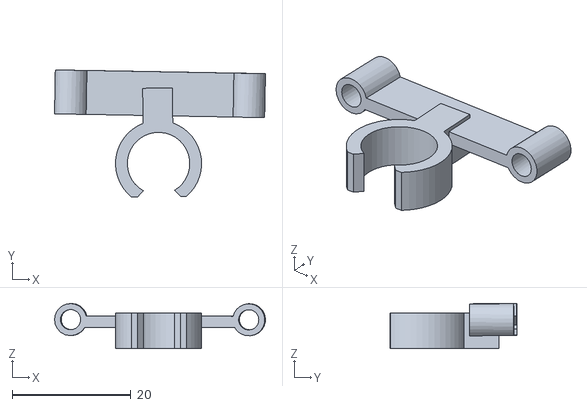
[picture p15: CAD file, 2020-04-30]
Mechanical_Designs/Sensor_Mount.stl
35.5 x 21.4 x 7.59

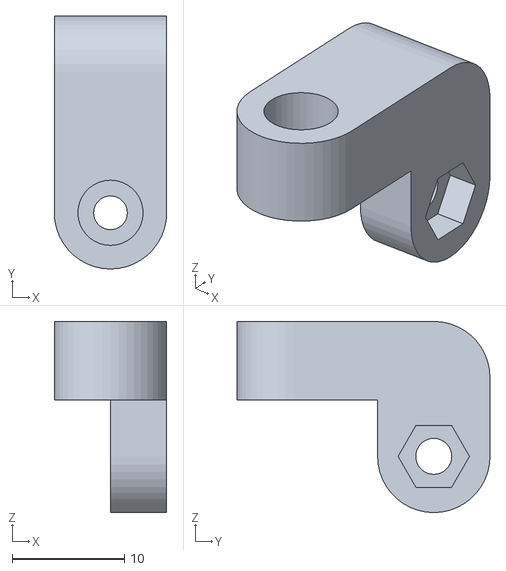
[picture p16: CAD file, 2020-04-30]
Mechanical_Designs/Arm_c.stl
10.0 x 22.5 x 17.0

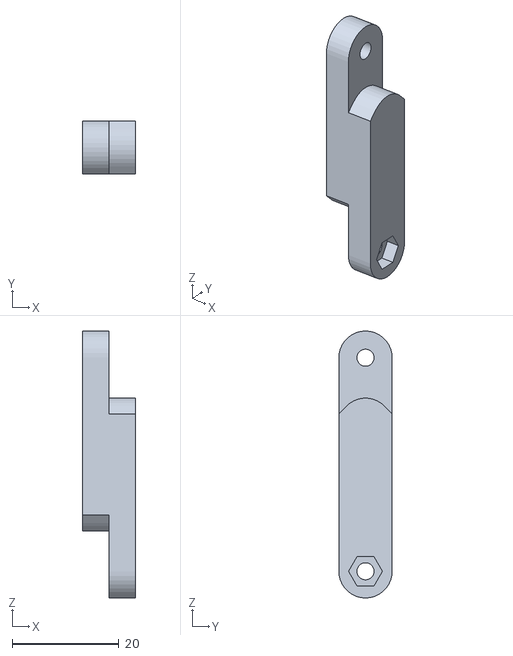
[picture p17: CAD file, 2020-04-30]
Mechanical_Designs/Arm_b.stl
10.0 x 10.0 x 50.0

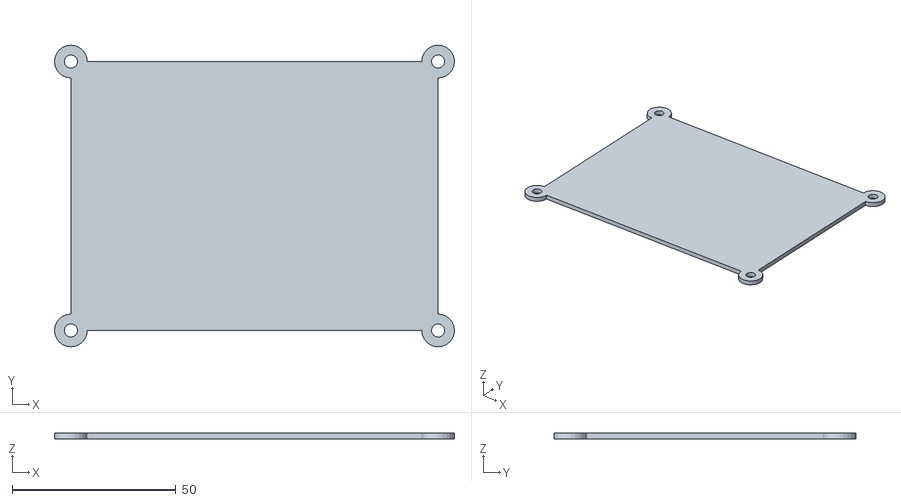
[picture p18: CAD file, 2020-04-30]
Mechanical_Designs/Case_top.stl
122.0 x 92.0 x 1.85

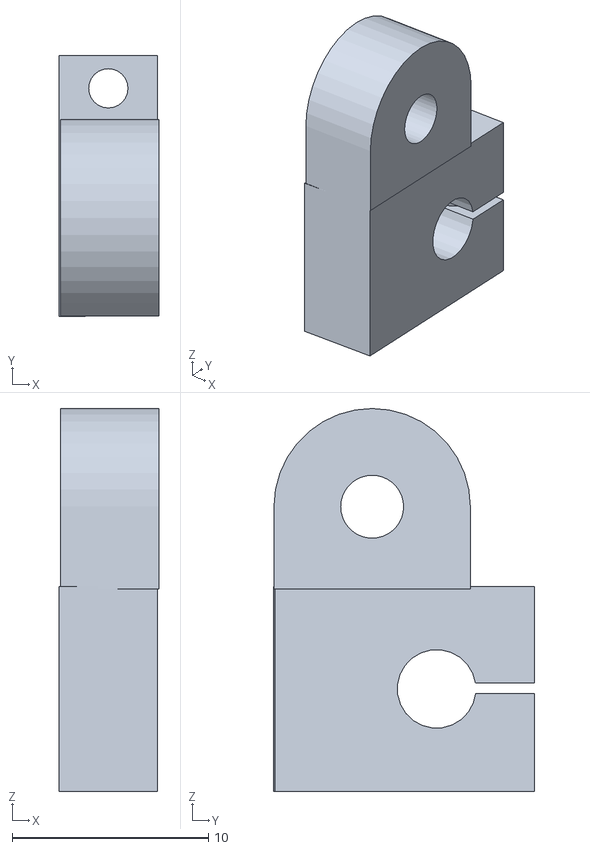
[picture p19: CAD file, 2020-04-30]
Mechanical_Designs/Arm_a.stl
5.07 x 13.3 x 19.5

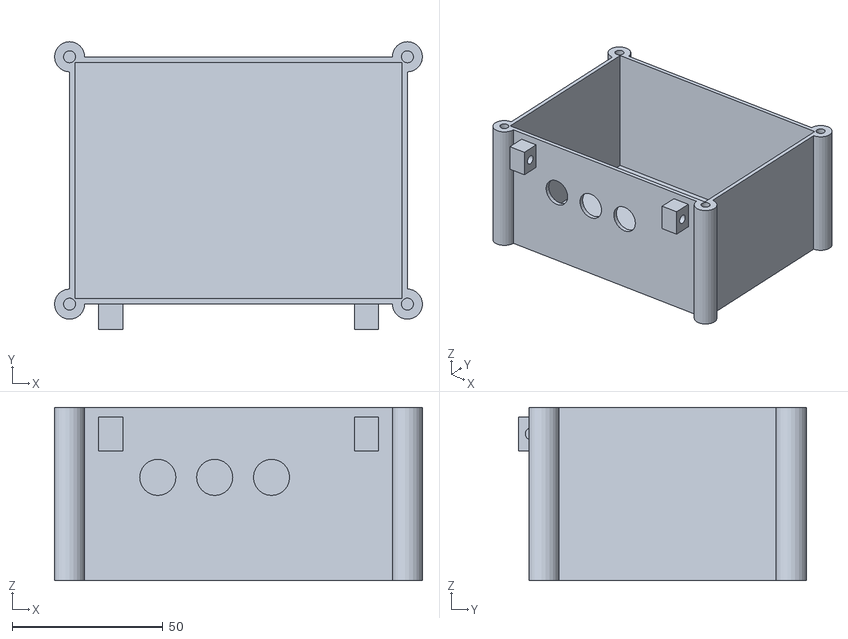
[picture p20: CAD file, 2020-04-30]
Mechanical_Designs/Case_bottom.stl
122.0 x 95.3 x 57.5

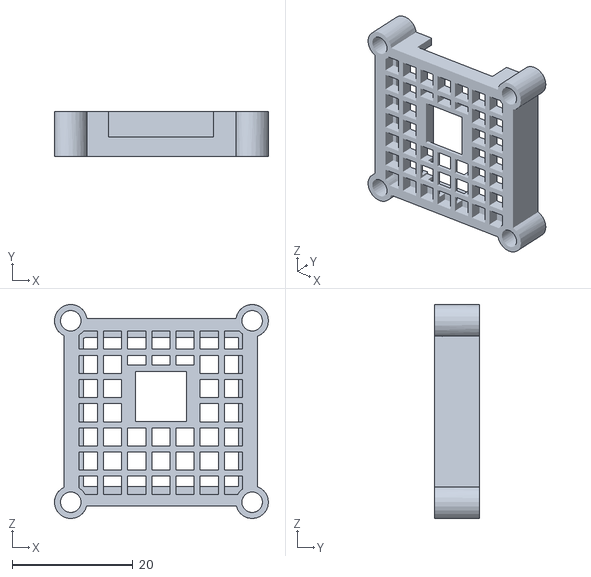
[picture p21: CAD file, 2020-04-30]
Mechanical_Designs/Camera_Mount.stl
35.4 x 7.40 x 35.4

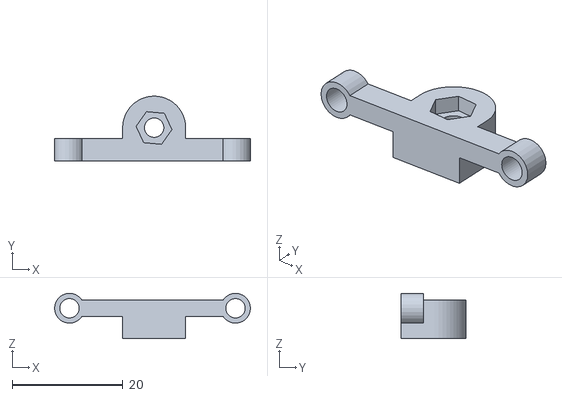
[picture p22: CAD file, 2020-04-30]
Mechanical_Designs/Arm_d.stl
35.4 x 11.7 x 8.20

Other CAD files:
Mechanical_Designs/Case.skp
Mechanical_Designs/Pi_camera_arm.skp
Mechanical_Designs/Sensor arm.skp

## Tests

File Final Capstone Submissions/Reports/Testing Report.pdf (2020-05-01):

Testing of Low Cost, Remote Data Acquisition Platform for In Situ Biological and Fluidic Measurements

Rachel Zaltz
Department of Computer Engineering The George Washington University Washington, DC,
United States of America
rachelzaltz@gwu.edu

Connor Kraft
Department of Computer Engineering The George Washington University Washington, DC,
United States of America
connorkraft3@gwu.edu

Phillip Jones
Department of Electrical Engineering The George Washington University Washington, DC,
United States of America
phillipjones116@gwu.edu

Abstract—A low-cost data acquisition platform will be designed and assembled to increase the ease of dynamic in situ data collection from confined isolated environments such as incubators. The aim of this project is to record humidity, temperature, PH, turbidity, time-stamped imaging, and various other sensor
data at user-specified intervals. The device will remain physically independent of the space outside the incubator by using a modular power supply and network connection. The device will run independently of a power supply for the duration of the experiment and wirelessly send the desired data to a remote user. The device will advance research in cellular and polymetric interactions with indirect measurement and imaging in incubators.
I. INTRODUCTION:
The low-cost data-acquisition platform will be designed to increase dynamic in situ data collection in confined and isolated environments. Currently, when an experiment is performed within an incubator for a long period of time, lab technicians are unable to open the confined environment until the experiment has been completed in its entirety. This results in a loss of crucial data points as the experiment is progressing within the incubator. Currently, the data cannot be obtained during the duration of the experiment and this results in the loss of many crucial data points. A low-cost data acquisition platform would increase data collection in in situ environments.

Currently, there are only a few products that solve the issue at hand. Some of the best products are from Dickson Data, such as the DicksonOne. These products only allow for a small set of sensors and lack more advanced sensor technology and cameras. They are also very expensive, with the cheapest model being $350. Each individual sensor costs over 100 dollars and requires a paid subscription to use some of the more advanced features. Overall, a product does not exist that meets all of the design requirements for this task.

This project looks to implement a system which can gather data within a closed incubator and send that data to a user on any remote computer. The data is gathered from multiple sensors including temperature, humidity, pH, turbidity, and time stamped images. This data is gathered at a time interval which can be specified by the user to allow for greater flexibility of the system. When data is not being gathered, sensors are turned off in order to save power and conserve energy. This data is then sent to a remote server using a Wifi connection so that it may be viewed by the user.

II. THEORY OF OPERATION
The goal of the project is to design a system which can gather data in a closed environment and send this data wirelessly to a remote user. The data gathered is specified by the sensors and the system is able to do this with only one input from the user, the data collection rate (every 30 seconds), and how long to gather data for (12 hours). These inputs and outputs are outlined in Figure I below.

At the current time, gathered data is collected and stored in labeled local directories on the Raspberry Pi. All relevant timestamps, sensor data, and image names are then queued by Redis and transferred to a SQL Server database running on the server. For the sake of redundancy, all relevant Raspberry Pi local files are then synced to a directory on this server.

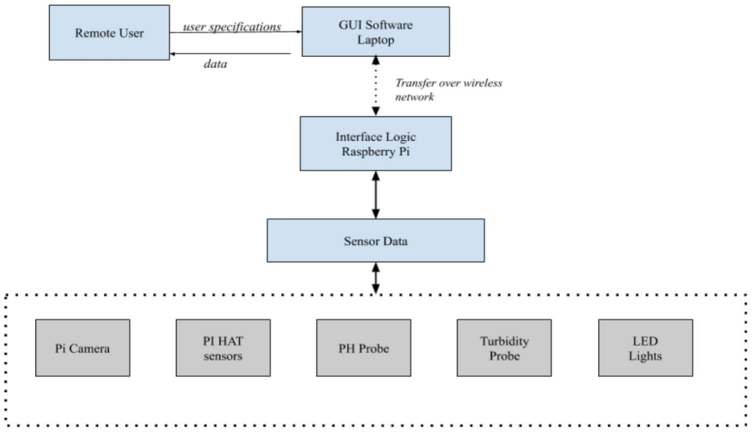
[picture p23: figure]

Figure I: Context Level Diagram

III. TESTING METHODS
This section outlines the testing
methods that were used to verify the performance of the Remote Data Acquisition Platform in accordance with the set specifications. The purpose of these tests is to measure the end-to-end performance of the device, and to identify any constraints in operation. Due to the current Coronavirus outbreak, several of the designed tests were not able to be run; this will be discussed below in individual testing sections and in the breakdown of specifications. Please note, the result of this is that several aspects of the specifications were not able to be verified at the current time.
A. Raspberry Pi and Sensors
The most comprehensive testing option available to assess the behavior and operation of the project’s data pipeline was to monitor system performance during fully-fledged application runs. Three tests were designed to exhibit system characteristics during what can be considered as a typical experimental operation.
The tests are as follows: 1 hour testing run with

360 samples (10 second poll interval), 2 hour 30 minute testing run with 50 samples (3 minute poll interval), and 8 hour 20 minute testing run with 100 samples (5 minute poll interval).

At each polling interval, system diagnostics will be gathered by recording the CPU usage, CPU temperature, and RAM usage. Due to the testing constraints, this test is largely qualitative, but provides key information about system health and operation. Each of the three tests will be run twice, to form an idea of system performance while idling and while running the designed application. The qualifications desired when looking at the overall comparison of dry versus loaded test runs are that the system stays under 85 degrees Celsius (particularly 80 degrees Celsius, as this is where thermal throttling begins), and that only marginal increases in average CPU and RAM usage occur going from dry to loaded test versions. Essentially, this testing acts as verification that the system performs as expected, and that the designed application does not overload the system in any way.
B. User Interface
The purpose of this test was to ensure the front end was properly connected to the server and there were no malfunctions. This test mimicked an experimental operation of a 1 hour testing run with 360 samples (10 second poll interval) and an 8 hour 20 minute testing run with 100 samples (5 minute poll interval). The purpose of the test was to ensure all data appeared in the front end GUI and no connection or data was Lost in the process.
C. Power Management
The purpose of this test was to estimate the power draw of the entire system to select a battery that would be able to last the entire length of an experiment. The test minicked an experiment lasting 4 weeks sampling once every minute in one experiment and sampling once every hour in the other.

TABLE I:
REQUIREMENTS AND SPECIFICATIONS
System Level Requirements: | System Level Specifications: | Test Results:
Operates with a lithium ion battery pack. | The device shall be able to run on a lithium ion battery pack. | Battery was not purchased due to COVID-19 impediments.
Have a long battery life so the device does not have to be removed from the incubator. | The device shall be able to last on the battery pack for the duration of the experiment (minimum 1 day - maximum 4 weeks). | Measurements were calculated (see results section in report).
Take pictures of the test environment. | A Pi camera must be used to take pictures of the test environment at user specified intervals. | This requirement was met (see code).
Have a light source for the test environment. | The device must conserve battery by only using the lights when needed (e.g., taking a picture) or when the user specifies. | This requirement was met (see code).
Conserve battery with 2 different modes: sleep and active. | The device shall be in sleep mode when measurements and images are not being taken. | Though this was not formalized, this was verified by testing in experiment-like circumstances.
Measure pH. | The device shall be able to measure the pH of the solution from 0 to 14 at +/-0.001 increments using a pH probe, with an accuracy of +/- 0.002. | This is confirmed by the data sheet found here. (https://www.atlas-scientific.com/_files/_datasheets/_probe/pH_probe.pdf)
Measure humidity and | The device shall be able to | This is confirmed by the data

temperature. | measure humidity from 20 to 80% with an accuracy of +/-5% and temperature from 0 to 50 degrees C with an accuracy of +/- 0.2 degrees C using an Adafruit DHT11/22 sensor. | sheet found here. (https://cdn-shop.adafruit.com/datasheets/DHT22.pdf)
Measure turbidity. | A turbidity probe shall be used to measure the amount of light scattered by the solids in the solution. | Not applicable, this sensor was not added to the array.
Measure electrical conductivity. | A conductivity probe shall be used to measure the electrical conductivity of the solution from 5 to 200,000 micro-S/cm, with an accuracy of +/-2%. | This is confirmed by the data sheet found here. (https://www.atlas-scientific.com/_files/_datasheets/_probe/EC_K_10_probe.pdf)
Be accessible to a remote user. | The device shall send data to a GUI that can be accessed remotely through a desktop and mobile application. | The data is available to a remote use if they have the code running on their laptop. The code was not deployed to the server (due to COVID-19).
Communication will be enabled via Wifi. | The device should be able to send data to a computer via the built in Wifi module on the Raspberry Pi 3+. | This requirement was met and demonstrated in the presentation.

IV. TEST RESULTS
I. Raspberry Pi and Sensors
At the very least, evidence in comparison between the dry and loaded run test qualitatively shows that the designed
application succeeds in its goal of being low impact. Through these tests, it can be definitively noted that the data pipeline performs exactly as suspected and that the application has little impact on system performance over time.
A short examination of the test results is as follows (all values are averages taken over the length of the experiment):
| ❏ Dry test results ❏ 1 hour test (360 samples)

❏ CPU temperature -
53.9 degrees Celsius
❏ CPU usage - 24.5 %
❏ RAM usage - 52.3 %
❏ 2 hour, 30 minute test (50 samples)
❏ CPU temperature -
54.9 degrees Celsius
❏ CPU usage - 25.8 %
❏ RAM usage - 52.6 %
❏ 8 hour, 20 minute test (100 samples)
❏ CPU temperature -
54.5 degrees Celsius
❏ CPU usage - 24.6 %

❏ RAM usage - 52.4 %
❏ Loaded test results
❏ 1 hour test
❏ CPU temperature -
56.9 degrees Celsius
❏ CPU usage - 26.6 %
❏ RAM usage - 74.1 %
❏ 2 hour, 30 minute test
❏ CPU temperature -
56.6 degrees Celsius
❏ CPU usage - 26.9 %
❏ RAM usage - 71.7 %
❏ 8 hour, 20 minute test
❏ CPU temperature -
58.4 degrees Celsius
❏ CPU usage - 28.2 %
❏ RAM usage - 72.9 %

Overall, even between short and long-term testing periods, the system shows expected changes when going from the dry to loaded tests. Average CPU usage and temperature experience a marginal increase when the system is under load, but nowhere near alarming values. CPU temperatures stay well below operational limits and do not come close to thermal throttling, in either case. Of note is the 20 % or so increase in RAM usage while under load, which is expected due to the implementation of the Redis queue in this project. This data convincingly verifies appropriate system performance under experiment-like load.

II. User Interface
The front end test was done for a 1 hour test and an 8 hour experiment. The results below show that data correctly flowed through the pipeline and was received on the front end side of the code.

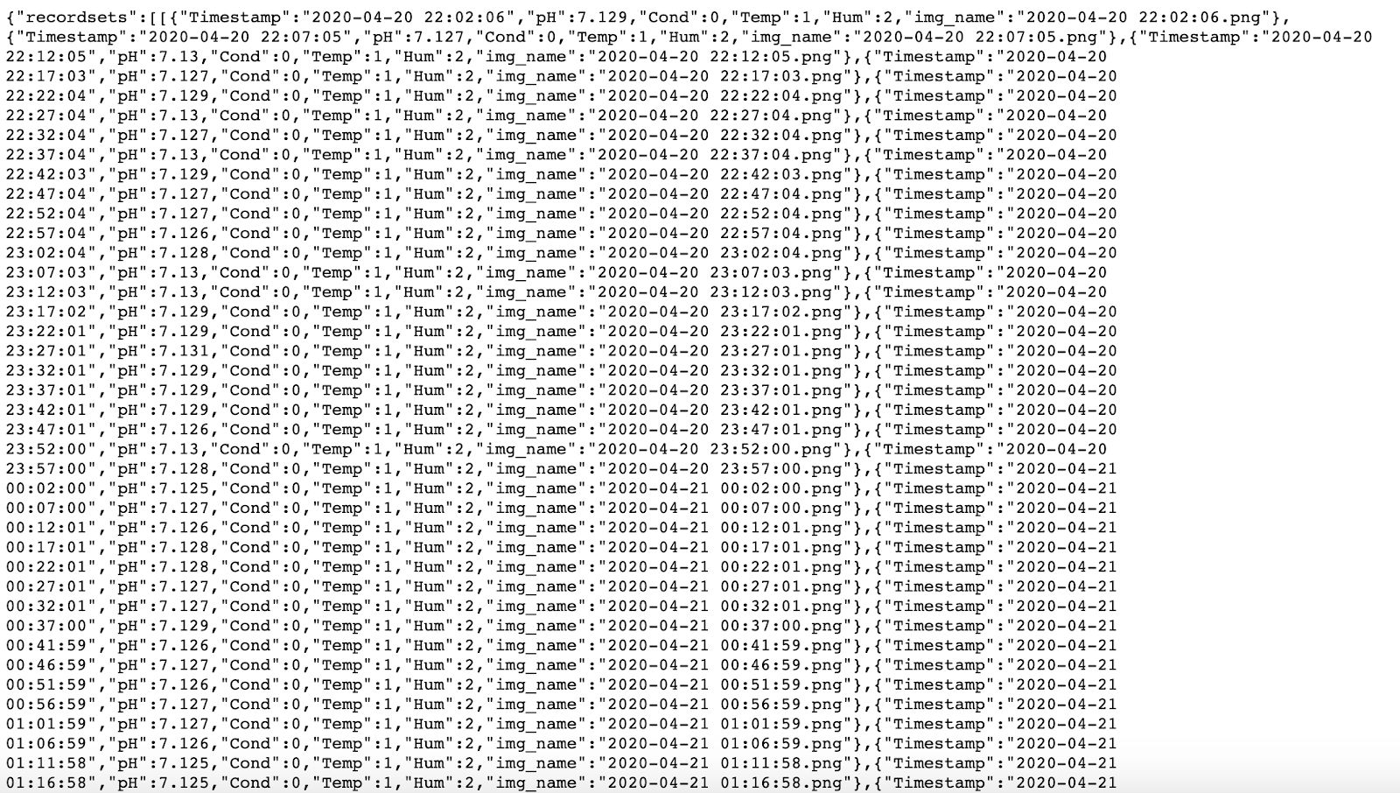
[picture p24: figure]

Figure II: Front End of 8 Hour Test

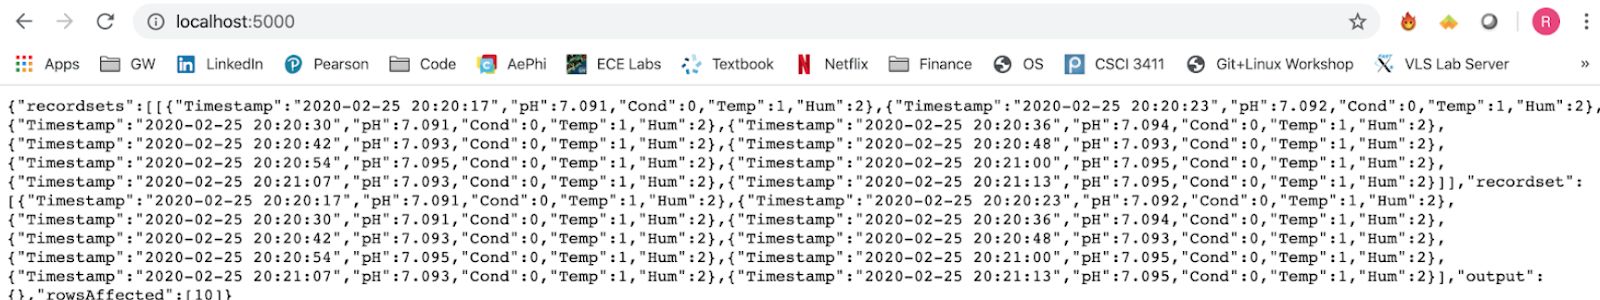
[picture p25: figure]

Figure III: Front End of 1 Hour Test

III. Power Management
The power draw test was estimated for 4 weeks taking data either every minute or every hour. The results show that a 440
Amp Hour battery is needed in order to last while collecting data every minute and a 290 Amp Hour battery is needed in order to last while collecting data every hour.

Figure IV: Power Draw of Components

Figure V: Sampling every minute

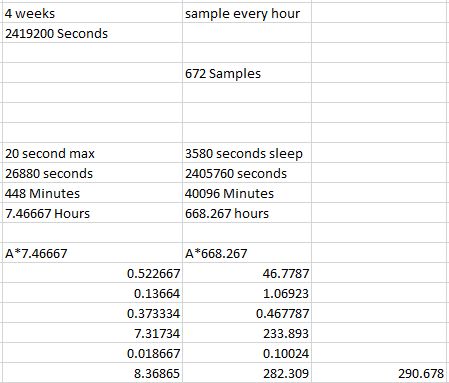
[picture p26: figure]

Figure VI: Sampling every Hour

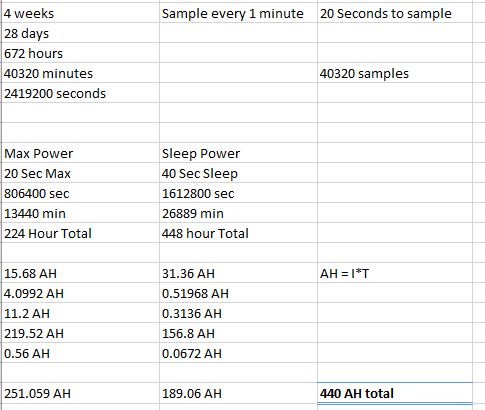
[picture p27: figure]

ACKNOWLEDGEMENT
This project would not be in its current state without the help of Professor Aslani and Professor Bulusuu
Additionally, the project was supported by the following departments: Electrical and Computer Engineering Department, Biofluid Dynamics Laboratory (PI: Prof. M. W. Plesniak), Department of Mechanical and Aerospace Engineering, and the Tissue Engineering Laboratory (PI: Prof. L. –G. Zhang), Department of Mechanical and Aerospace Engineering.
REFERENCES
Conductivity Probe K10 Datasheet. (n.d.). Retrieved from https://www.atlas-scientific.com/_files/_datasheets/_probe/EC_K_10_probe.pdf
Lab Grade pH Probe Datasheet. (n.d.). Retrieved from https://www.atlas-scientific.com/_files/_datasheets/_probe/pH_probe.pdf
Digital Output Relative Humidity & Temperature Sensor/Module Datasheet. (n.d.). Retrieved from https://cdn-shop.adafruit.com/datasheets/DHT22.pdf

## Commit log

2020-01-22 Add files via upload
    This is an updated version for implementation of Atlas Scientific Sensors. Please note, this is not currently working and needs to be revised.
2020-03-03 Run4 - Current Working Version
